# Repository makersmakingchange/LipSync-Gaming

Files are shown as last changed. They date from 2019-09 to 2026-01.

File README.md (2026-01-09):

## LipSync Gaming

> [!IMPORTANT]
**As of 2024-Feb-08, this version of the LipSync is now obsolete and has been replaced by the [LipSync 4](https://github.com/makersmakingchange/LipSync).**

The LipSync Gaming is an assistive technology device that allows quadriplegics and other people with limited hand function to use touchscreen mobile devices, tablets, and computers by manipulation of a mouth-operated joystick with integrated sip and puff controls. This is an Open-Source Hardware project, so the LipSync can be made at the community level for less than $300.

## Compatibility 

 <table style="width:100%">
  <tr>
    <th>Operating Systems</th>
    <th>Version</th>
    <th>Release</th>
    <th>Additional Information</th>
  <tr>
    <td>iOS</td>
    <td>13.1</td>
    <td>September 19,2019</td>
    <td>Compatible with iPhone 7 and newer versions (Requires USB to Lightning or USB to USB-C Adapter)</td>
  </tr>
  <tr>
    <td>Windows</td>
    <td>XP,7,10</td>
    <td>2001</td>
    <td>Compatible with Windows XP and newer versions</td>
  </tr>
  <tr>
    <td>Android</td>
    <td>4-9</td>
    <td>Released 2013</td>
    <td>Compatible with Android 4 and newer versions (Requires USB On-The-Go)</td>
  </tr>
  <tr>
    <td>MacOS</td>
    <td>10</td>
    <td>Released 2000</td>
    <td>Compatible with Mac OS X 10.0 and newer versions</td>
  </tr>
  </table> 

## Download

 <table style="width:100%">
  <tr>
    <th>Resource</th>
    <th>Version</th>
    <th>Format</th>
    <th>Link</th>
  </tr>
    <tr>
    <td>LipSync Gaming All</td>
    <td>3.0</td>
    <td>ZIP</td>
    <td><a href="https://github.com/makersmakingchange/LipSync-Gaming/archive/refs/heads/main.zip">LipSync-Gaming.zip</a></td>
  </tr>
  <tr>
    <td>LipSync Assembly Guide</td>
    <td>1.6</td>
    <td>PDF</td>
    <td><a href="https://github.com/makersmakingchange/LipSync-Gaming/blob/main/Documentation/LipSync_Assembly_Guide.pdf">LipSync_Assembly_Guide.pdf</a></td>
  </tr>
  <tr>
    <td>LipSync Gaming Startup Guide</td>
    <td>1.4</td>
    <td>PDF</td>
    <td><a href="https://github.com/makersmakingchange/LipSync-Gaming/blob/main/Documentation/LipSync_Gaming_Startup_Guide.pdf">LipSync_Gaming_Startup_Guide.pdf</a></td>
  </tr>
  <tr>
    <td>LipSync Gaming User Guide</td>
    <td>1.4</td>
    <td>PDF</td>
    <td><a href="https://github.com/makersmakingchange/LipSync-Gaming/blob/main/Documentation/LipSync_Gaming_User_Guide.pdf">LipSync_Gaming_User_Guide.pdf</a></td>
  </tr>
  <tr>
     <td>LipSync Gaming Mounting Guide</td>
     <td>1.0</td>
     <td>PDF</td>
     <td><a href="https://github.com/makersmakingchange/LipSync-Gaming/blob/main/Documentation/LipSync_Mounting_Guide.pdf">LipSync_Mounting_Guide.pdf</a></td>
  </tr>
  <tr>
    <td>LipSync Gaming BOM (XLSX)</td>
    <td>September 1, 2021</td>
    <td>XLSX</td>
    <td><a href="https://github.com/makersmakingchange/LipSync-Gaming/blob/main/Documentation/LipSync_Gaming_BOM.xlsx">LipSync_Gaming_BOM.xlsx</a></td>
  </tr>
  <tr>
    <td>LipSync Gaming BOM (CSV)</td>
    <td>September 1, 2021</td>
    <td>CSV</td>
    <td><a href="https://github.com/makersmakingchange/LipSync-Gaming/blob/main/Documentation/LipSync_Gaming_BOM.csv">LipSync_Gaming_BOM.csv</a></td>
  </tr>
  <tr>
    <td>LipSync Gaming Firmware</td>
    <td>3.0</td>
    <td>INO</td>
    <td><a href="https://raw.githubusercontent.com/makersmakingchange/LipSync-Gaming/main/Software/LipSync_Gaming_Firmware/LipSync_Gaming_Firmware.ino">LipSync_Gaming_Firmware.ino</a></td>
  </tr>
  <tr>
    <td>LipSync Gaming Interface Board Layout</td>
    <td>2.71</td>
    <td>BRD</td>
    <td><a href="https://github.com/makersmakingchange/LipSync-Gaming/raw/main/Hardware/PCB_design/Eagle/LipSync_Interface_Board/LipSync_Interface_Board.brd">LipSync_Interface_Board.brd</a></td>
  </tr>
  <tr>
    <td>LipSync Gaming Interface Board Schematic</td>
    <td>2.71</td>
    <td>SCH</td>
    <td><a href="https://raw.githubusercontent.com/makersmakingchange/LipSync-Gaming/main/Hardware/PCB_design/Eagle/LipSync_Interface_Board/LipSync_Interface_Board.sch">LipSync_Interface_Board.sch</a></td>
  </tr>
  <tr>
    <td>JLCPCB LipSync Gaming Interface Board Gerber</td>
    <td>2.71</td>
    <td>ZIP</td>
    <td><a href="https://github.com/makersmakingchange/LipSync-Gaming/raw/main/Hardware/PCB_design/Gerber/LipSync_Interface_Board/JLCPCB_LipSync_Interface_Board.zip">JLCPCB_LipSync_Interface_Board.zip</a></td>
  </tr>
  <tr>
    <td>OSHPark LipSync Gaming Interface Board Gerber</td>
    <td>2.71</td>
    <td>ZIP</td>
    <td><a href="https://github.com/makersmakingchange/LipSync-Gaming/raw/main/Hardware/PCB_design/Gerber/LipSync_Interface_Board/OSHPark_LipSync_Interface_Board.zip">OSHPark_LipSync_Interface_Board.zip</a></td>
  </tr>
  <tr>
    <td>PCBWay LipSync Gaming Interface Board Gerber</td>
    <td>2.71</td>
    <td>ZIP</td>
    <td><a href="https://github.com/makersmakingchange/LipSync-Gaming/raw/main/Hardware/PCB_design/Gerber/LipSync_Interface_Board/PCBWay_LipSync_Interface_Board.zip">PCBWay_LipSync_Interface_Board.zip</a></td>
  </tr>
  <tr>
    <td>Seeed Fusion LipSync Gaming Interface Board Gerber</td>
    <td>2.71</td>
    <td>ZIP</td>
    <td><a href="https://github.com/makersmakingchange/LipSync-Gaming/raw/main/Hardware/PCB_design/Gerber/LipSync_Interface_Board/Seeed_Fusion_LipSync_Interface_Board.zip">Seeed_Fusion_LipSync_Interface_Board.zip</a></td>
  </tr>
  <tr>
    <td rowspan="9">Housing_design</td>
    <td rowspan="9">3.0</td>
    <td rowspan="9">STL</td>
    <td><a href="https://github.com/makersmakingchange/LipSync-Gaming/blob/main/Hardware/Housing_design/LipSync_Button.stl">LipSync_Button.STL</a></td>
  </tr>
  <tr>
  <td><a href="https://github.com/makersmakingchange/LipSync-Gaming/blob/main/Hardware/Housing_design/LipSync_Front_Housing.STL">LipSync_Front_Housing.STL</a></td>
  </tr>
  <tr>
	<td><a href="https://github.com/makersmakingchange/LipSync-Gaming/blob/main/Hardware/Housing_design/LipSync_Joystick_Base.STL">LipSync_Joystick_Base.STL</a></td>
</tr>
<tr>
  <td><a href="https://github.com/makersmakingchange/LipSync-Gaming/blob/main/Hardware/Housing_design/LipSync_Joystick_Front.STL">LipSync_Joystick_Front.STL</a></td>
</tr>
<tr>
  <td><a href="https://github.com/makersmakingchange/LipSync-Gaming/blob/main/Hardware/Housing_design/LipSync_Joystick_Rocker.STL">LipSync_Joystick_Rocker.STL</a></td>
</tr>
<tr>
    <td><a href="https://github.com/makersmakingchange/LipSync-Gaming/blob/main/Hardware/Housing_design/Optional/LipSync_Joystick_Jig.STL">LipSync_Joystick_Jig.STL</a></td>
</tr>
<tr>
  <td><a href="https://github.com/makersmakingchange/LipSync-Gaming/blob/main/Hardware/Housing_design/LipSync_Rear_Housing.STL">LipSync_Rear_Housing.STL</a></td>
</tr>
<tr>
  <td><a href="https://github.com/makersmakingchange/LipSync-Gaming/blob/main/Hardware/Housing_design/3D_Print_Settings.txt">3D_Print_Settings.txt</a></td>
</tr>
</table> 

## Resources

<table style="width:100%">
  <tr>
    <th>Resource</th>
    <th>Link</th>
  </tr>
  <tr>
    <td>LipSync Firmware and Calibration Video</td>
    <td><a href="https://www.youtube.com/watch?v=RnpA24WH0Qk">Video</a></td>
  <tr>
    <td>LipSync Joystick Calibration Video</td>
    <td><a href="https://www.youtube.com/watch?v=Daf-54y6SBg">Video</a></td>
  </tr>
    <tr>
    <td>LipSync Build Video</td>
    <td><a href="https://www.youtube.com/watch?v=lBXpbkp5DW4&list=PLhoPg9bDvBR4CSFRfNbQ87ALnfaHOyM3C">Video</a></td>
  </tr>
</table> 

## License
Copyright (c) 2018-2024 Neil Squire / Makers Making Change.

This repository describes Open Hardware:
 - Everything needed or used to design, make, test, or prepare the LipSync Gaming is licensed under the [CERN 2.0 Weakly Reciprocal license (CERN-OHL-W v2) or later](https://cern.ch/cern-ohl ) .
 - All software is under the [GNU General Public License v3.0 (GPL-3.0)](https://www.gnu.org/licenses/gpl.html).
 - Accompanying material such as instruction manuals, videos, and other copyrightable works that are useful but not necessary to design, make, test, or prepare the LipSync are published under a [Creative Commons Attribution-ShareAlike 4.0 license (CC BY-SA 4.0)](https://creativecommons.org/licenses/by-sa/4.0/) .

You may redistribute and modify this documentation and make products using it under the terms of the [CERN-OHL-W v2](https://cern.ch/cern-ohl).
This documentation is distributed WITHOUT ANY EXPRESS OR IMPLIED WARRANTY, INCLUDING OF MERCHANTABILITY, SATISFACTORY QUALITY AND FITNESS FOR A PARTICULAR PURPOSE.
Please see the CERN-OHL-W v2 for applicable conditions.

Source Location: https://github.com/makersmakingchange/LipSync-Wireless

## Attribution

The LipSync Gaming was designed by Neil Squire Society / Makers Making Change. The initial development of a 3D printable LipSync was supported by the Google Impact Challenge: Disabilities grant from Google.org. Further development was supported through the Government of Canada's Innovation Science and Economic Development Assistive Technology Program. These and other funders have also enabled Neil Squire / Makers Making Change to deploy numerous LipSyncs to users at reduced cost.

The LipSync firmware utilizes the Arduino development platform, an open-source electronics platform based on easy-to-use hardware and software. Arduino is developed and maintained by the Arduino community, and the project wouldn't be possible without their contributions.
Arduino is a registered trademark of Arduino AG. For more information about Arduino and to contribute to the community, visit the official Arduino website at www.arduino.cc.

### Contributors
 - Milad Hajihassan, Neil Squire Society / Makers Making Change.
 - Jake McIvor, Neil Squire Society / Makers Making Change.
 - Kristina Mok, Neil Squire Society / Makers Making Change.
  
----

<!-- ABOUT MMC START -->
## About Makers Making Change
[Makers Making Change Logo](https://www.makersmakingchange.com/)

Makers Making Change is a program of [Neil Squire](https://www.neilsquire.ca/), a Canadian non-profit that uses technology, knowledge, and passion to empower people with disabilities.

Makers Making Change leverages the capacity of community based Makers, Disability Professionals and Volunteers to develop and deliver affordable Open Source Assistive Technologies.

 - Website: [www.MakersMakingChange.com](https://www.makersmakingchange.com/)
 - GitHub: [makersmakingchange](https://github.com/makersmakingchange)
 - Bluesky: [@makersmakingchange.bsky.social](https://bsky.app/profile/makersmakingchange.bsky.social)
 - Instagram: [@makersmakingchange](https://www.instagram.com/makersmakingchange)
 - Facebook: [makersmakechange](https://www.facebook.com/makersmakechange)
 - LinkedIn: [Neil Squire Society](https://www.linkedin.com/company/neil-squire-society/)
 - Thingiverse: [makersmakingchange](https://www.thingiverse.com/makersmakingchange/about)
 - Printables: [MakersMakingChange](https://www.printables.com/@MakersMakingChange)

### Contact Us
For technical questions, to get involved, or to share your experience we encourage you to [visit our website](https://www.makersmakingchange.com/) or [contact us](https://www.makersmakingchange.com/s/contact).
<!-- ABOUT MMC END -->

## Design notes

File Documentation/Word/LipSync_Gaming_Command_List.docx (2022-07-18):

## LipSync Gaming Command List

Command | Success Response | Failure Response | Description
SETTINGS | SUCCESS,0:SETTINGS | FAIL,{N}: Command | Enter Settings mode
EXIT | SUCCESS,0:EXIT | FAIL,{N}: Command | Exit Settings mode
MN,0:0 | SUCCESS,0:MN,0:2 | FAIL,{N}:Command | Get Model number (2=Gaming)
VN,0:0 | SUCCESS,0:VN,0:V{N.NN} | FAIL,{N}:Command | Get version number (V{N.NN})
SS,0:0 | SUCCESS,0:SS,0:{Joystick Sensitivity Level} | FAIL,{N}:Command | Get the joystick sensitivity value (Level)
SS,1:{Joystick Sensitivity Level:0-10} | SUCCESS,0:SS,1:{Joystick Sensitivity Level} | FAIL,{N}:Command | Set the joystick sensitivity value (Level)
| MANUAL,0:SS,1:{Joystick Sensitivity Level} | | Set the joystick sensitivity value (Level)
PT,0:0 | SUCCESS,0:PT,0:{Threshold 5% to 50%}:{Nominal Pressure V*100} | FAIL,{N}:Command | Get puff pressure threshold (threshold 5% to 50%) (Nominal Pressure)
PT,1:{threshold 10% to 50%} | SUCCESS,0:PT,1:{Threshold 5% to 50%}:{ Nominal Pressure V*100} | FAIL,{N}:Command | Set puff pressure threshold (threshold 5% to 50%) (Nominal Pressure)
ST,0:0 | SUCCESS,0:PT,0:{Threshold 5% to 50%}:{Nominal Pressure V*100} | FAIL,{N}:Command | Get sip pressure threshold (threshold 5% to 50%) (Nominal Pressure)
ST,1:{threshold 5% to 50%} | SUCCESS,0:PT,1:{Threshold 5% to 50%}:{ Nominal Pressure V*100} | FAIL,{N}:Command | Set sip pressure threshold (threshold 5% to 50%) (Nominal Pressure)
PV,0:0 | SUCCESS,0:PV,0:{Nominal Pressure} | FAIL,{N}:Command | Get pressure value (Nominal Pressure)
RA,0:0 | SUCCESS,0:RA,0:{Rotation Angle} | FAIL,{N}:Command | Get rotation angle (deg)
RA,1:{Angle: 0-359} | SUCCESS,0:RA,1:{Rotation Angle} | FAIL,{N}:Command | Set rotation angle (0,90,180,270 deg)
DM,0:0 | SUCCESS,0:DM,0:{Debug Mode} | FAIL,{N}:Command | Get debug mode value ( 0=debug mode disabled,1=debug mode enabled)
DM,1:0 | SUCCESS,0:DM,1:0 | FAIL,{N}:Command | Set debug mode value to 0 (Disabled)
DM,1:1 | SUCCESS,0:DM,1:1 | FAIL,{N}:Command | Set debug mode value to 1 (Enabled)
| LOG,1:{0,0,0,xHighNeutral,xLowNeutral,yHighNeutral,yLowNeutral} | | Log initialization values once if debug mode is enabled
| LOG,2:{0,0,0,xHighMax,xLowMax,yHighMax,yLowMax} | | Log calibration values once if debug mode is enabled
| LOG,3:{x,y,action,xHigh,xLow,yHigh,yLow} | | Log cursor and FSR values if debug mode is enabled until debug mode is disabled
IN,0:0 | SUCCESS,0:IN,0:{xHighNeutral,xLowNeutral,yHighNeutral,yLowNeutral} | FAIL,{N}:Command | Get joystick initialization values (xHighNeutral,xLowNeutral,yHighNeutral,yLowNeutral)
IN,1:1 | SUCCESS,0:IN,1:{xHighNeutral,xLowNeutral,yHighNeutral,yLowNeutral} | FAIL,{N}:Command | Perform joystick initialization using command (xHighNeutral,xLowNeutral,yHighNeutral,yLowNeutral)
| MANUAL,0:IN,1:{xHighNeutral,xLowNeutral,yHighNeutral,yLowNeutral} | | Perform joystick initialization using push button or sip/puff (xHighNeutral, xLowNeutral,yHighNeutral,yLowNeutral)
JV,0:0 | SUCCESS,0:JV,0:{xHigh,xLow,yHigh,yLow} | FAIL,{N}:Command | Get joystick FSR values: {xHigh,xLow,yHigh,yLow}
CA,0:0 | SUCCESS,0:CA,0:{xHighMax,xLowMax,yHighMax,yLowMax} | FAIL,{N}:Command | Get joystick calibration values (xHighMax,xLowMax,yHighMax,yLowMax)
CA,1:1 | SUCCESS,0:CA,1:0 | FAIL,{N}:Command | Perform joystick calibration using command
| SUCCESS,0:CA,1:1 | FAIL,{N}:Command | Perform joystick calibration using command (Step 1)
| SUCCESS,0:CA,1:2 | FAIL,{N}:Command | Perform joystick calibration using command (Step 2)
| SUCCESS,0:CA,1:3 | FAIL,{N}:Command | Perform joystick calibration using command (Step 3)
| SUCCESS,0:CA,1:4 | FAIL,{N}:Command | Perform joystick calibration using command (Step 4)
| SUCCESS,0:CA,1:5:{xHighMax,xLowMax,yHighMax,yLowMax} | FAIL,{N}:Command | Perform joystick calibration using command (Step 5) (xHighMax,xLowMax,yHighMax,yLowMax)
| MANUAL,0:CA,1:0 | | Perform joystick calibration using push button
| MANUAL,0:CA,1:1 | | Perform joystick calibration using push button (Step 1)
| MANUAL,0:CA,1:2 | | Perform joystick calibration using push button (Step 2)
| MANUAL,0:CA,1:3 | | Perform joystick calibration using push button (Step 3)
| MANUAL,0:CA,1:4 | | Perform joystick calibration using push button (Step 4)
| MANUAL,0:CA,1:5:{xHighMax,xLowMax,yHighMax,yLowMax} | | Perform joystick calibration using push button (Step 5) (xHighMax,xLowMax,yHighMax,yLowMax)
MP,0:0 | SUCCESS,0:MP,0:{NNNNNN} | FAIL,{N}:Command | Get Button mapping ( Example: SUCCESS,0:MP,0:125670)
MP,1: {NNNNNN} | SUCCESS,0:MP,1:{NNNNNN} | FAIL,{N}:Command | Set Button mapping ( Example: MP,1:125670)
DZ,0:0 | SUCCESS,0:DZ,0:{Deadzone Value} | FAIL,{N}:Command | Get the deadzone value
DZ,1:{ Deadzone :30-250} | SUCCESS,0:DZ,1:{ Deadzone Value} | FAIL,{N}:Command | Set the deadzone value ( Example: SUCCESS,0:DZ,1:30)
BM,0:0 | SUCCESS,0:BM,0:{Button Mode Value} | FAIL,{N}:Command | Get the button mode value (1 = Digital Mode , 2 = Analog Mode)
BM,1:{ Button Mode Value:1-2} | SUCCESS,0:BM,1:{Button Mode Value} | FAIL,{N}:Command | Set the button mode value (1 = Digital Mode , 2 = Analog Mode)
FR,1:{Rest Type: 0-1} | SUCCESS,0:FR,1:{Reset Type: 0-1} | FAIL,{N}:Command | Perform factory reset (0 = Hard Reset , 1 = Soft Reset)

## API Format

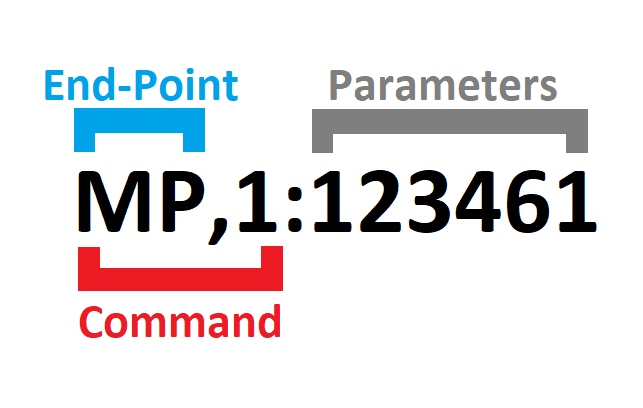
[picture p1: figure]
The API format which includes the end-point, command ,and the parameters.

## Response Code

Response Status | Response Code | Description
SUCCESS | 0 | The command has successfully performed.
FAIL | 0 | The serial API mode is not enabled. Please enter the serial API mode.
FAIL | 1 | The requested command does not exist. Returns the response code and the requested parameter.
FAIL | 2 | The requested command exists, but the entered parameter is in incorrect format. Returns the response code and the requested parameter.
FAIL | 3 | The requested command exists, but the entered parameter is out of range. Returns the response code and the current value stored in the EEPROM.

## Input Actions

Input Action | Description
Short Puff | < 3 seconds
Short Sip | < 3 seconds
Long Puff | 3-5 seconds
Long Sip | 3-5 seconds
Very Long Puff | > 5 seconds
Very Long Sip | > 5 seconds

## Output Digital Actions

Action Number | Output Action | Description
0 | (No action) | No action
1 | Button 1 Click | Presses and immediately releases Button 1.
2 | Button 2 Click | Presses and immediately releases Button 2.
3 | Button 3 Click | Presses and immediately releases Button 3.
4 | Button 4 Click | Presses and immediately releases Button 4.
5 | Button 5 Click | Presses and immediately releases Button 5.
6 | Button 6 Click | Presses and immediately releases Button 6.
7 | Center Reset | Initiates center reset routine to set joystick center position.
8 | Calibration | Initiates joystick calibration routine to set joystick limits and reset joystick center.

## Output Analog Actions

Action Number | Output Action | Description
0 | (No action) | No action
1 | Button 1 Press | Presses Button 1.
2 | Button 2 Press | Presses Button 2.
3 | Button 3 Press | Presses Button 3.
4 | Button 4 Press | Presses Button 4.
5 | Button 5 Press | Presses Button 5.
6 | Button 6 Press | Presses Button 6.
7 | Center Reset | Initiates center reset routine to set joystick center position.
8 | Calibration | Initiates joystick calibration routine to set joystick limits and reset joystick center.

## Digital Action Mapping

Input Action | LipSync Gaming Action
Short Puff | 1 : Button 1 Press and Release
Short Sip | 2 : Button 2 Press and Release
Long Puff | 5 : Button 5 Press and Release
Long Sip | 6 : Button 6 Press and Release
Very Long Puff | 7 : Center Reset
Very Long Sip | 0 : No action

## Analog Action Mapping

Input Action | LipSync Gaming Action
Puff | 1 : Button 1 Press
Sip | 2 : Button 2 Press

## Example

INPUT | RESPONSE | ACTION
SETTINGS | SUCCESS,0:SETTINGS | LipSync Ready for API Command
VN,0:0 | SUCCESS,0:VN,0:30 | LipSync return firmware version 3.0

INPUT | RESPONSE | ACTION
SETTINGS | SUCCESS,0:SETTINGS | LipSync Ready for API Command
PT,0:0 | SUCCESS,0:PT,0:10 | LipSync return current puff pressure threshold of 10%
PT,1:20 | FAIL,0:PT,1:20 | (Attempt to set puff pressure threshold failed – need to resend SETTINGS for each command)
SETTINGS | SUCCESS,0:SETTINGS | LipSync Ready for API Command
PT,1:20 | SUCCESS,0:PT,1:20:266 | LipSync set new puff pressure threshold of 20% and returned current nominal pressure of

Makers Making Change LipSync Gaming Command List

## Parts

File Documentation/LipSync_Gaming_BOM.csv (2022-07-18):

Qty | Component | Component name (September 1, 2021) | Line Item | Manufacturer | COO | MPN | SKU | SKU | SKU | SKU | SKU | SKU | SKU | SKU | URL ( Canada ) | URL ( United States )
 |  |  |  |  |  |  | Digi-Key | Mouser | Qosina | Cole-Parmer | Lee Spring | U.S. Plastic Corp. | B&H Photo | Amazon
1 | Required | Arduino Micro | A000053 | Arduino | Italy | A000053 | 1050-1066-ND | 782-A000053 |  |  |  |  |  |  | https://www.digikey.ca/product-detail/en/arduino/A000053/1050-1066-ND | https://www.digikey.com/product-detail/en/arduino/A000053/1050-1066-ND
2 | Required | Right Angle Push Button | "431256058736" | Würth Elektronik | China | "431256058736" | 431256058736-ND |  |  |  |  |  |  |  | http://www.digikey.ca/product-detail/en/wurth-electronics-inc/431256058736/431256058736-ND | https://www.digikey.com/product-detail/en/wurth-electronics-inc/431256058736/431256058736-ND
2 | Required | 300 Ohm 1/4W Axial Through-Hole Resistor | CF14JT300R | Stackpole Electronics | China | CF14JT300R | CF14JT300RCT-ND |  |  |  |  |  |  |  | https://www.digikey.ca/product-detail/en/stackpole-electronics-inc/CF14JT300R/CF14JT300RCT-ND | https://www.digikey.com/product-detail/en/stackpole-electronics-inc/CF14JT300R/CF14JT300RCT-ND
4 | Required | 10k Ohm 1/4W Mini Axial Through-Hole Resistor | CFM14JT10K0 | Stackpole Electronics | China | CFM14JT10K0 | S10KQCT-ND |  |  |  |  |  |  |  | https://www.digikey.ca/product-detail/en/stackpole-electronics-inc/CFM14JT10K0/S10KQCT-ND/ | https://www.digikey.com/product-detail/en/stackpole-electronics-inc/CFM14JT10K0/S10KQCT-ND/
1 | Required | Pressure Transducer | MPXV7002DPT1 | NXP Semiconductors | Malaysia | MPXV7002DPT1 | MPXV7002DPT1CT-ND | 841-MPXV7002DP |  |  |  |  |  |  | https://www.digikey.ca/product-detail/en/freescale-semiconductor-nxp/MPXV7002DPT1/MPXV7002DPT1CT-ND | https://www.digikey.com/product-detail/en/freescale-semiconductor-nxp/MPXV7002DPT1/MPXV7002DPT1CT-ND
1 | Required | 0.01 uF Ceramic Through-Hole Radial Capacitor | C315C103K5R5TA | KEMET | Mexico | C315C103K5R5TA | 399-4148-ND | 80-C315C103K5R |  |  |  |  |  |  | http://www.digikey.ca/product-detail/en/kemet/C315C103K5R5TA7303/399-9858-1-ND | http://www.digikey.com/product-detail/en/kemet/C315C103K5R5TA7303/399-9858-1-ND
1 | Required | 1.0 uF Ceramic Through-Hole Radial Capacitor | C315C105K3R5TA | KEMET | Mexico | C315C105K3R5TA | 399-9714-ND | 80-C315C105K3R |  |  |  |  |  |  | http://www.digikey.ca/product-detail/en/kemet/C315C105K3R5TA/399-9714-ND | http://www.digikey.com/product-detail/en/kemet/C315C105K3R5TA/399-9714-ND
1 | Required | 470 pF Ceramic Through-Hole Radial Capacitor | C315C471K5R5TA | KEMET | Mexico | C315C471K5R5TA | 399-9740-ND | 80-C315C471K5R |  |  |  |  |  |  | http://www.digikey.ca/product-detail/en/kemet/C315C471K5R5TA/399-9740-ND | http://www.digikey.com/product-detail/en/kemet/C315C471K5R5TA/399-9740-ND
2 | Required | 17-Position Straight Female Through-Hole Headers | PPPC171LFBN-RC | Sullins | Taiwan | PPPC171LFBN-RC | S7050-ND |  |  |  |  |  |  |  | http://www.digikey.ca/product-detail/en/sullins-connector-solutions/PPPC171LFBN-RC/S7050-ND | http://www.digikey.com/product-detail/en/sullins-connector-solutions/PPPC171LFBN-RC/S7050-ND
2 | Required | 3-Position Right Angle Male Through-Hole Header | 22-05-2031 | Molex | Mexico | 22-05-2031 | WM4101-ND |  |  |  |  |  |  |  | https://www.digikey.ca/product-detail/en/molex-connector-corporation/22-05-2031/WM4101-ND/ | https://www.digikey.com/product-detail/en/molex-connector-corporation/22-05-2031/WM4101-ND/
2 | Required | 3-Position Straight Female Through-Hole Header | 801-87-003-10-001101 | Preci-Dip | Switzerland | 801-87-003-10-001101 | 1212-1180-ND |  |  |  |  |  |  |  | https://www.digikey.ca/product-detail/en/preci-dip/801-87-003-10-001101/1212-1180-ND | https://www.digikey.com/product-detail/en/preci-dip/801-87-003-10-001101/1212-1180-ND
2 | Required | 4-Position Straight Female Through-Hole Header | PPPC041LFBN-RC | Sullins | Taiwan | PPPC041LFBN-RC | S7037-ND |  |  |  |  |  |  |  | http://www.digikey.ca/product-detail/en/sullins-connector-solutions/PPPC041LFBN-RC/S7037-ND | https://www.digikey.com/product-detail/en/sullins-connector-solutions/PPPC041LFBN-RC/S7037-ND
1 | Required | 40-Position Breakaway Straight Male Through-Hole Headers | PRPC040SAAN-RC | Sullins | Taiwan | PRPC040SAAN-RC | S1011EC-40-ND |  |  |  |  |  |  |  | http://www.digikey.ca/product-detail/en/sullins-connector-solutions/PRPC040SAAN-RC/S1011EC-40-ND | http://www.digikey.com/product-detail/en/sullins-connector-solutions/PRPC040SAAN-RC/S1011EC-40-ND
1 | Required | 5mm Bi-Color Through-Hole LED | MV5437 | Everlight Electronics Co Ltd | China | MV5437 | 1080-1109-ND |  |  |  |  |  |  |  | https://www.digikey.ca/product-detail/en/everlight-electronics-co-ltd/MV5437/1080-1109-ND/2675600 | https://www.digikey.com/product-detail/en/everlight-electronics-co-ltd/MV5437/1080-1109-ND/2675601
1 | Required | Jumper Shunt Connector | SSC02SYAN | Sullins | Taiwan | SSC02SYAN | S9002-ND |  |  |  |  |  |  |  | https://www.digikey.ca/product-detail/en/sullins-connector-solutions/SPC02SYAN/S9002-ND | https://www.digikey.com/product-detail/en/sullins-connector-solutions/SPC02SYAN/S9002-ND
1 | Required | 2N3906 PNP-type Through-Hole Transistor | 2N3906TFR | Fairchild Semiconductor | China | 2N3906TFR | 2N3906D26ZCT-ND |  |  |  |  |  |  |  | http://www.digikey.ca/product-detail/en/fairchild-on-semiconductor/2N3906TFR/2N3906D26ZCT-ND | http://www.digikey.com/product-detail/en/fairchild-on-semiconductor/2N3906TFR/2N3906D26ZCT-ND
1 | Required | 6-Position Straight Female Through-Hole Header | PPPC061LFBN-RC | Sullins | Taiwan | PPPC061LFBN-RC | S7039-ND |  |  |  |  |  |  |  | https://www.digikey.ca/product-detail/en/sullins-connector-solutions/PPPC061LFBN-RC/S7039-ND | https://www.digikey.com/product-detail/en/sullins-connector-solutions/PPPC061LFBN-RC/S7039-ND
1 | Required | Sip and Puff Mouthpiece | "11648" | Qosina | USA | "80102" |  |  | "80102" |  |  |  |  |  | https://www.qosina.com/stepped-male-luer-lock-connector-80102 | https://www.qosina.com/stepped-male-luer-lock-connector-80102
1 | Required | Filter PTFE Hydrophobic 17 mm, 0.2 Micron | "28213" | Qosina | USA | "28213" |  |  | "28213" |  |  |  |  |  | http://www.qosina.com/hydrophobic-filter-with-female-luer-lock-inlet-male-luer-lock-outlet-28213 | http://www.qosina.com/hydrophobic-filter-with-female-luer-lock-inlet-male-luer-lock-outlet-28213
1 | Required | Luer Lock Fitting | RK-45508-32 | Cole-Parmer | USA | RK-45508-32 |  |  |  | RK-45508-32 |  |  |  |  | https://www.coleparmer.ca/i/cole-parmer-female-luer-bulkhead-1-4-28-unf-thread-to-3-32-hose-barb-pp-25-pk/4550832 | https://www.coleparmer.ca/i/cole-parmer-female-luer-bulkhead-1-4-28-unf-thread-to-3-32-hose-barb-pp-25-pk/4550832
4 | Required | Force Resistive Sensor | 30-49649 | Interlink Electronics | China | 30-49649 | 1027-1000-ND |  |  |  |  |  |  |  | http://www.digikey.ca/product-detail/en/interlink-electronics/30-49649/1027-1000-ND | http://www.digikey.com/product-detail/en/interlink-electronics/30-49649/1027-1000-ND
4 | Required | Screws Phillips Head M3 | NMS-308 | Würth Elektronik | China | 97790803211 | 732-13710-ND |  |  |  |  |  |  |  | https://www.digikey.ca/en/products/detail/w%C3%BCrth-elektronik/97790803211/10056393 | https://www.digikey.com/en/products/detail/w%C3%BCrth-elektronik/97790803211/10056393
6 | Required | Compression Spring | LC 016C 03 S | Lee Spring | China | LC 016C 03 S |  |  |  |  | LC 016C 03 S |  |  |  | https://www.leespring.com/compression-springs?search=LC016C03S | https://www.leespring.com/compression-springs?search=LC016C03S
2 | Required | Standoff M3 10mm | "25501" | Keystone | USA | "25501" | 36-25501-ND | 534-25501 |  |  |  |  |  |  | http://www.digikey.ca/product-detail/en/keystone-electronics/25501/36-25501-ND/ | http://www.digikey.com/product-detail/en/keystone-electronics/25501/36-25501-ND/
2 | Required | Standoff M3 15mm | "25503" | Keystone | USA | "25503" | 36-25503-ND | 534-25503 |  |  |  |  |  |  | http://www.digikey.ca/product-detail/en/keystone-electronics/25503/36-25503-ND/ | http://www.digikey.com/product-detail/en/keystone-electronics/25503/36-25503-ND/
1 | Required | Luer Lock Nut | 45509-04 | Cole-Parmer | USA | 45509-04 |  |  |  | 45509-04 |  |  |  |  | https://www.coleparmer.ca/i/cole-parmer-panel-mount-lock-nut-1-4-28-unf-black-nylon-25-pk/4550904 | https://www.coleparmer.ca/i/cole-parmer-panel-mount-lock-nut-1-4-28-unf-black-nylon-25-pk/4550904
4 | Required | Bumper | SJ-5003 (BLACK) | 3M | USA | SJ-5003 (BLACK) | SJ5003-0-ND | 517-SJ-5003BK |  |  |  |  |  |  | https://www.mouser.ca/ProductDetail/3M-Electronic-Specialty/SJ-5003-BLACK?qs=sGAEpiMZZMvlOED0T0kTWubpGv7E7tyx | https://www.digikey.com/product-detail/en/3m/SJ-5003-(BLACK)/SJ5003-0-ND/102574
4 | Required | Nut M3 | 4708 | Keystone Electronics | Taiwan | 4708 | 36-4708-ND |  |  |  |  |  |  |  | https://www.digikey.ca/product-detail/en/keystone-electronics/4708/36-4708-ND/4499301 | https://www.digikey.com/product-detail/en/keystone-electronics/4708/36-4708-ND/4499301
1 | Required | Tubing Tygon 3350 3/32" ID x 45mm | "57289" | Tygon® | USA | "57289" |  |  |  |  |  | "57289" |  |  | http://www.usplastic.com/catalog/item.aspx?itemid=31562&catid=864 | http://www.usplastic.com/catalog/item.aspx?itemid=31562&catid=864
2 | Required | Light Pipe | 51513030250F | Dialight | Malaysia | 51513030250F | 350-3746-ND | 645-515-1303-0250F |  |  |  |  |  |  | http://www.mouser.com/search/ProductDetail.aspx?r=645-515-1303-0250F | http://www.mouser.com/search/ProductDetail.aspx?r=645-515-1303-0250F
1 | Required | Threaded Insert 5/8”-27 | M-11 | WindTech | USA | M-11 |  |  |  |  |  |  | WIM11 |  | https://www.bhphotovideo.com/c/product/850285-REG/windtech_m_11_5_8_27_f_to_1_2_m_npt.html | https://www.adorama.com/wtm11.html
1 | Required | Threaded Adapter 5/8"-27 | Mic Adapter | CAMVATE | China | Mic Adapter |  |  |  |  |  |  |  | Mic Adapter | https://www.amazon.com/CAMVATE-Female-Male-Piece-Adapter/dp/B01GWVQ022 | https://www.amazon.com/CAMVATE-Female-Male-Piece-Adapter/dp/B01GWVQ022
1 | Required | USB Cable 3' or 6' | UUSBHAUB3RA | Startech | China | UUSBHAUB3RA |  |  |  |  |  |  |  | USB Cable 3' or 6' | https://www.amazon.ca/Startech-Com-UUSBHAUB3RA-Micro-Cable-Right/dp/B001AR4NC8 | https://www.amazon.com/StarTech-com-Micro-USB-Cable-UUSBHAUB3RA/dp/B001AR4NC8 | https://www.amazon.com/gp/huc/view.html?ie=UTF8&newItems=C50dc2962-6371-4880-bf41-06ac5db860d9%2C1 | https://www.amazon.com/gp/product/B01M18TDO1/ref=ox_sc_act_title_2?smid=A21TE5CLHZDYA7&psc=1
1 | Required | USB Splitter | USB Splitter | JIUWU | China | USB Splitter |  |  |  |  |  |  |  | USB Splitter | https://www.amazon.ca/Wpeng-Female-degree-Micro-Splitter/dp/B01M5F47SY | https://www.amazon.com/Micro-Female-Cable-Power-Splitter/dp/B00NSBVNCM
1 | Required | Cable Tie | 298-1021-ND | Panduit Corp | Singapore | PLT.6SM-M |  | 644-PLT.6SM-M |  |  |  |  |  |  | https://www.mouser.ca/ProductDetail/Panduit/PLT6SM-M | https://www.mouser.com/ProductDetail/Panduit/PLT6SM-M
1 | Optional | Magic Arm 11" and Clamp | ZC462800 | YKS / GkGk | China | ZC462800 |  |  |  |  |  |  |  | Magic Arm 11" and Clamp | https://www.amazon.com/GkGk-Articulating-Friction-Adjustable-Monitor/dp/B017HKJVL4/ | https://www.amazon.com/GkGk-Articulating-Friction-Adjustable-Monitor/dp/B017HKJVL4/

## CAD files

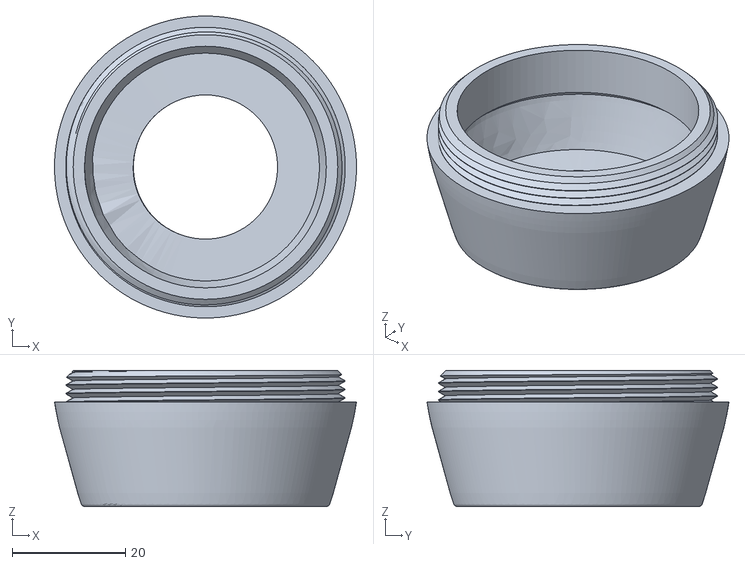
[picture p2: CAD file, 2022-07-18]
Hardware/Housing_design/LipSync_Front_Housing.STL
53.4 x 53.4 x 24.1

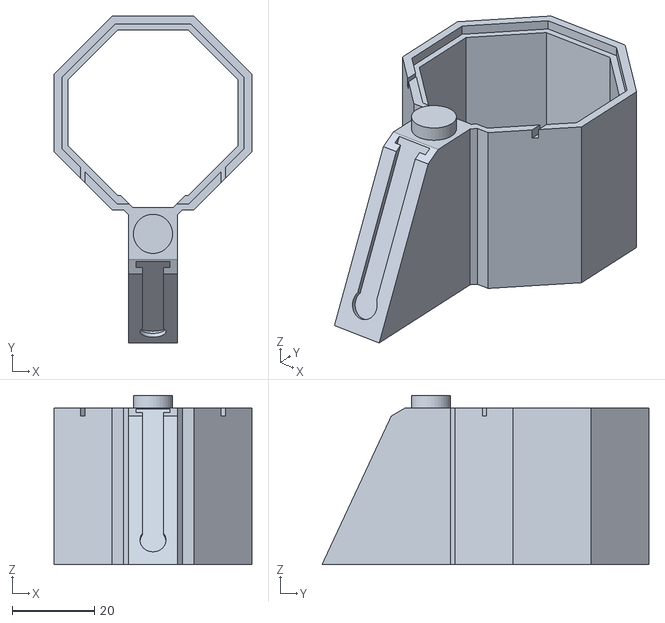
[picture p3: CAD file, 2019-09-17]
Hardware/Housing_design/Optional/LipSync_Joystick_Jig.STL
48.0 x 79.3 x 41.0

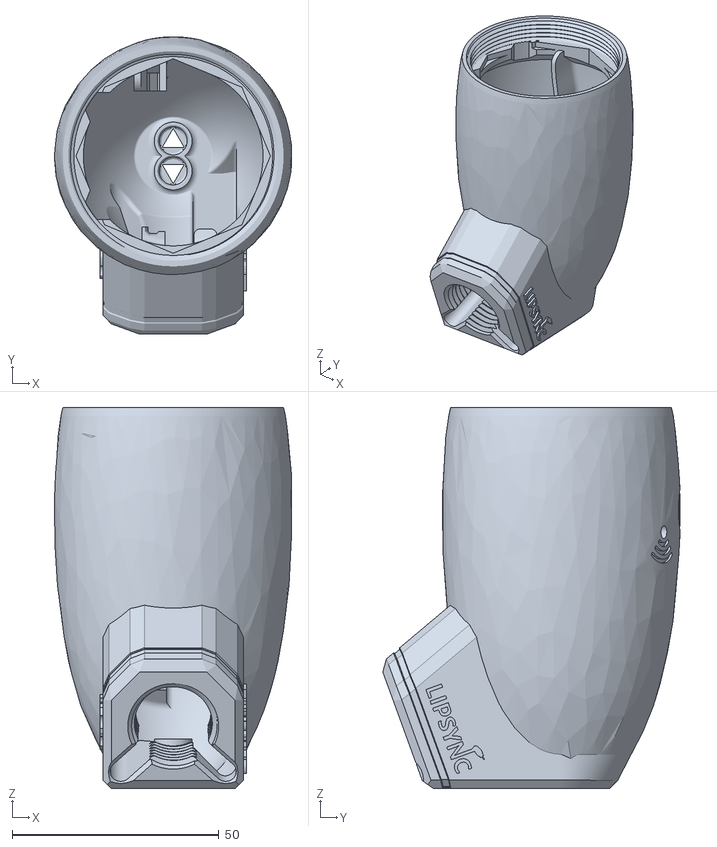
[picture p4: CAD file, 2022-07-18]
Hardware/Housing_design/LipSync_Rear_Housing.STL
57.5 x 72.0 x 92.2

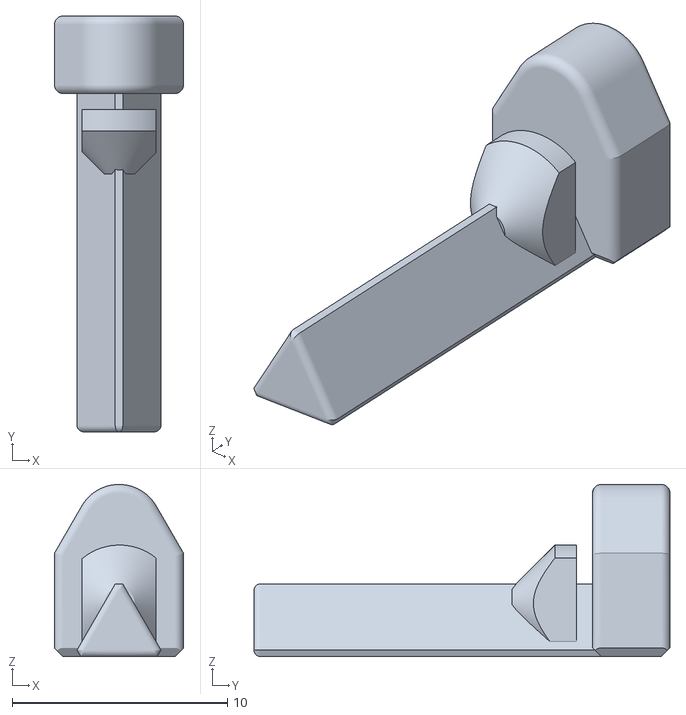
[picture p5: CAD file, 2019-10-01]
Hardware/Housing_design/LipSync_Button.stl
6.00 x 19.3 x 8.00

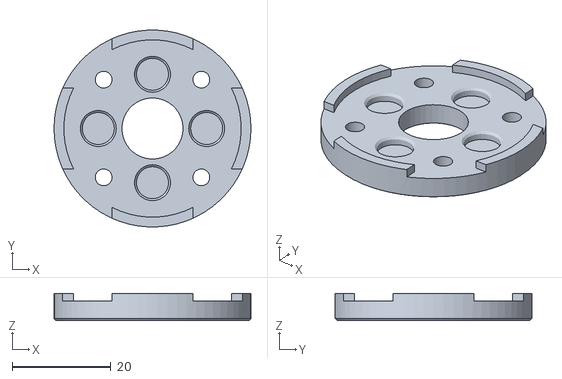
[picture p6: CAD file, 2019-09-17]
Hardware/Housing_design/LipSync_Joystick_Front.STL
40.0 x 39.9 x 5.50

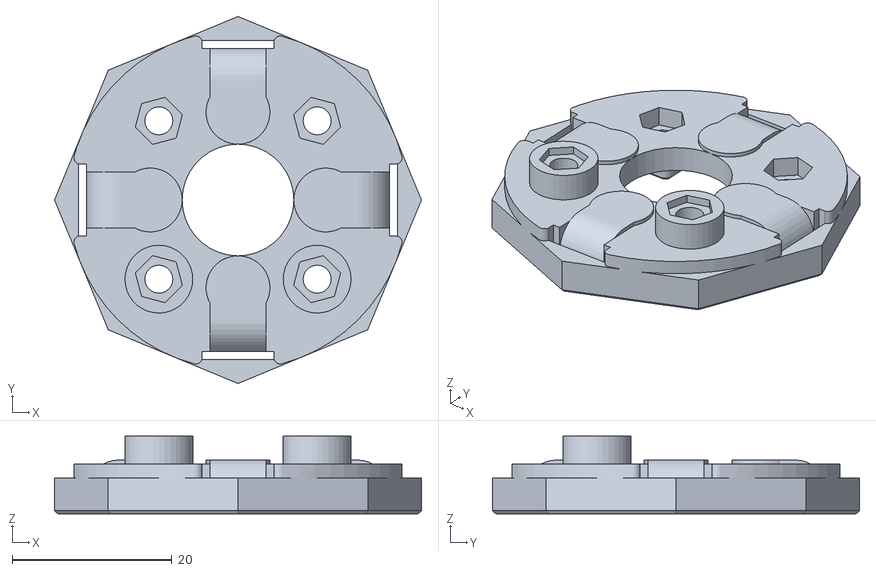
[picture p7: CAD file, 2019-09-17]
Hardware/Housing_design/LipSync_Joystick_Base.STL
46.0 x 46.0 x 9.75

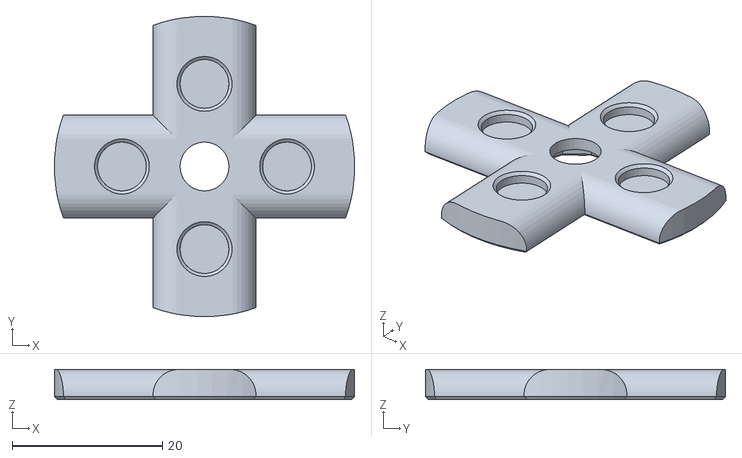
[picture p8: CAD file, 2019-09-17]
Hardware/Housing_design/LipSync_Joystick_Rocker.STL
40.0 x 40.0 x 4.00

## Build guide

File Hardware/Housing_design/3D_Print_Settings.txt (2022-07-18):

Print all components in orientation of STL file. Parts are designed to print with a 0.40 mm nozzle. Neutral, non-obtrusive filament colors (e.g. black, grey, white) are preferred for the rear housing and front housing unless the user requests otherwise. 

----------------------------
First print:
LipSync_Rear_Housing

Infill: 20%
Layer Height: 0.2mm
Support Material: No
Raft: No
Walls: 3
----------------------------

----------------------------
Second print:
1X LipSync_Front_Housing
2X LipSync_Button 
1X LipSync_Joystick_Stand (Optional; Recommended)

Infill: 20%
Layer Height: 0.2mm
Support Material: No
Raft: No
----------------------------

----------------------------
Third print:
1X LipSync_Joystick_Front_Plate
1X LipSync_Joystick_Rocker
1X LipSync_Joystick_Base

Infill: 50%
Layer Height: 0.2mm
Support Material: Yes
Raft: No
----------------------------

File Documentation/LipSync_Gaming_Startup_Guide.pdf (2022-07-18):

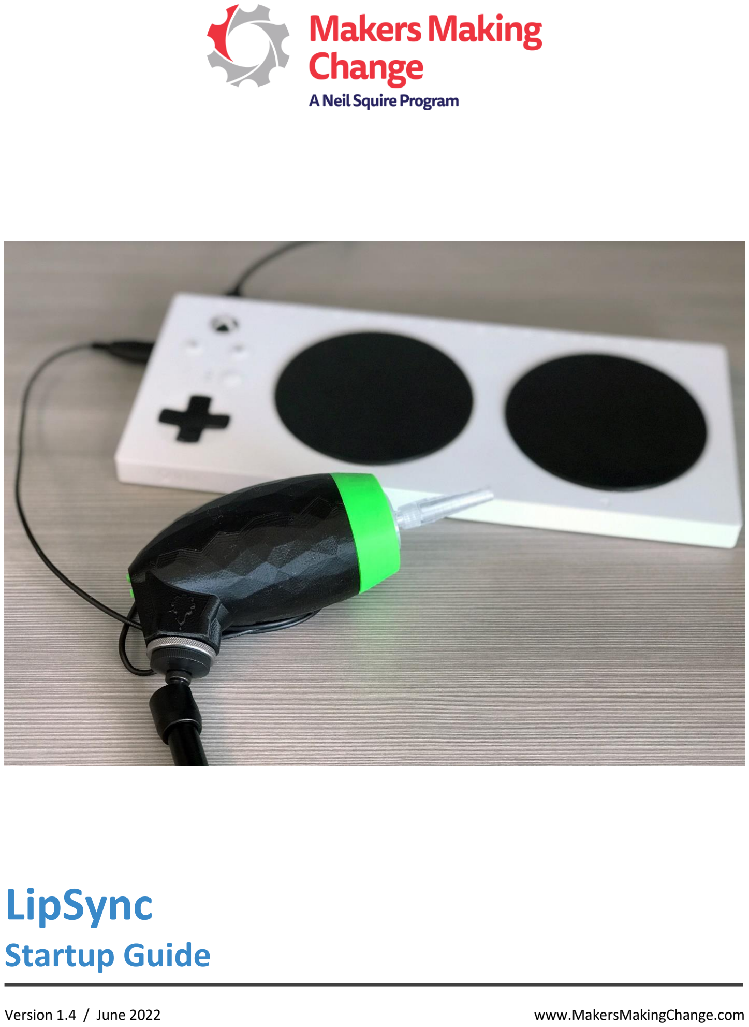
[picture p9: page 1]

# LipSync

# Startup Guide

Version 1.

4 / June 202

2 | www.MakersMakingChange.com

# Table of Contents

What Do You Get? | 3
Types of LipSync | 3
Mounting | 6
Device Compatibility | 7
Powering the Controller | 7
Sensitivity Control | 7
Setting Up for PC Gaming | 8
Functions (PC Games): | 8
Setting up for Xbox Gaming with the Xbox Adaptive Controller | 9
Functions (Xbox Adaptive Controller): | 9
Custom Profile | 10
Cleaning the Mouthpiece and Filter | 12
Cleaning the LipSync Shell | 13
Joystick Calibration | 14

# About the LipSync Gaming

The LipSync Gaming emulates a gaming controller for PC gaming and the Xbox console. Users can move the

mouthpiece up, down, left, and right; and use the sip-and-puff for other controller functions. This adaptive gaming

device is suitable for users with limited or no hand and finger dexterity. It can be paired with auxiliary controllers,

like the XBOX Adaptive Controller, to suit a gamer’s needs.

It is an open source assistive technology design by Makers Making Change, a program of the Neil Squire Society that

connects volunteer makers with people with disabilities to create more affordable assistive technology. Join the

Makers Makers Making Change to help people in your community: http://www.makersmakingchange.com

### What Do You Get?

### Types of LipSync

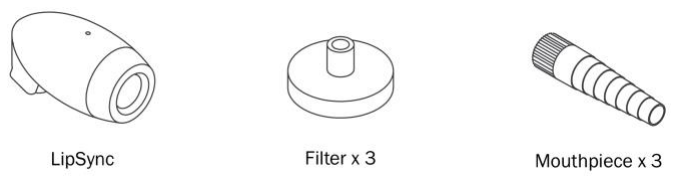
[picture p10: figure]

| Description | Connection Type
LipSync | Works like a mouse | USB
LipSync Wireless | Works like a mouse | Wireless
LipSync Macro | Works like a keyboard | USB & wireless
LipSync Gaming | Works like a gaming joystick | USB

# 1 LipSync Gaming Firmware Installation

1. Download and install the latest version of Arduino IDE: https://www.arduino.cc/en/main/software
2. Visit the LipSync Gaming firmware page: https://github.com/makersmakingchange/LipSync-

Gaming/raw/master/Software/LipSync_Gaming_Firmware/LipSync_Gaming_Firmware.ino (https://github.com/makersmakingchange/LipSync-Gaming/raw/master/Software/LipSync_Gaming_Firmware/LipSync_Gaming_Firmware.ino)

3. Right click on the webpage and select Save Page As. Add an .ino extension to the file name and click Save.
4. Visit the ArduinoJoystickLibrary GitHub repository using following link:

https://github.com/MHeironimus/ArduinoJoystickLibrary

5. Download the ArduinoJoystickLibrary by clicking on Clone or Download button and then selecting Download

ZIP option.

6. Extract the "ArduinoJoystickLibrary-master.zip" file.
7. Copy the Joystick folder to the Arduino libraries folder. An example of path to Arduino libraries folder in

Windows: C:\Program Files (x86)\Arduino\libraries

8. Once the folder is copied, the Joystick library should appear in the Arduino IDE list of libraries.
9. Plug the LipSync USB cable into the computer port.
10. Open Arduino IDE and you should be able to see Joystick examples under File > Examples > Joystick
11. Now open the LipSync_Gaming_Firmware.ino file using Arduino IDE.
12. Select Tools > Board > Arduino/Genuino Micro.
13. Select Tools > Port > COM## (number may be different for each user)
14. Click on upload button to upload the code.

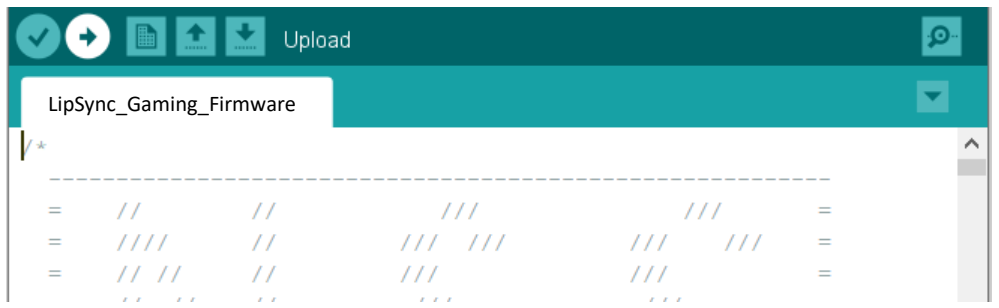
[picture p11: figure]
LipSync_Gaming_Firmware

15. With the LipSync Gaming plugged into a power source, perform the joystick calibration.

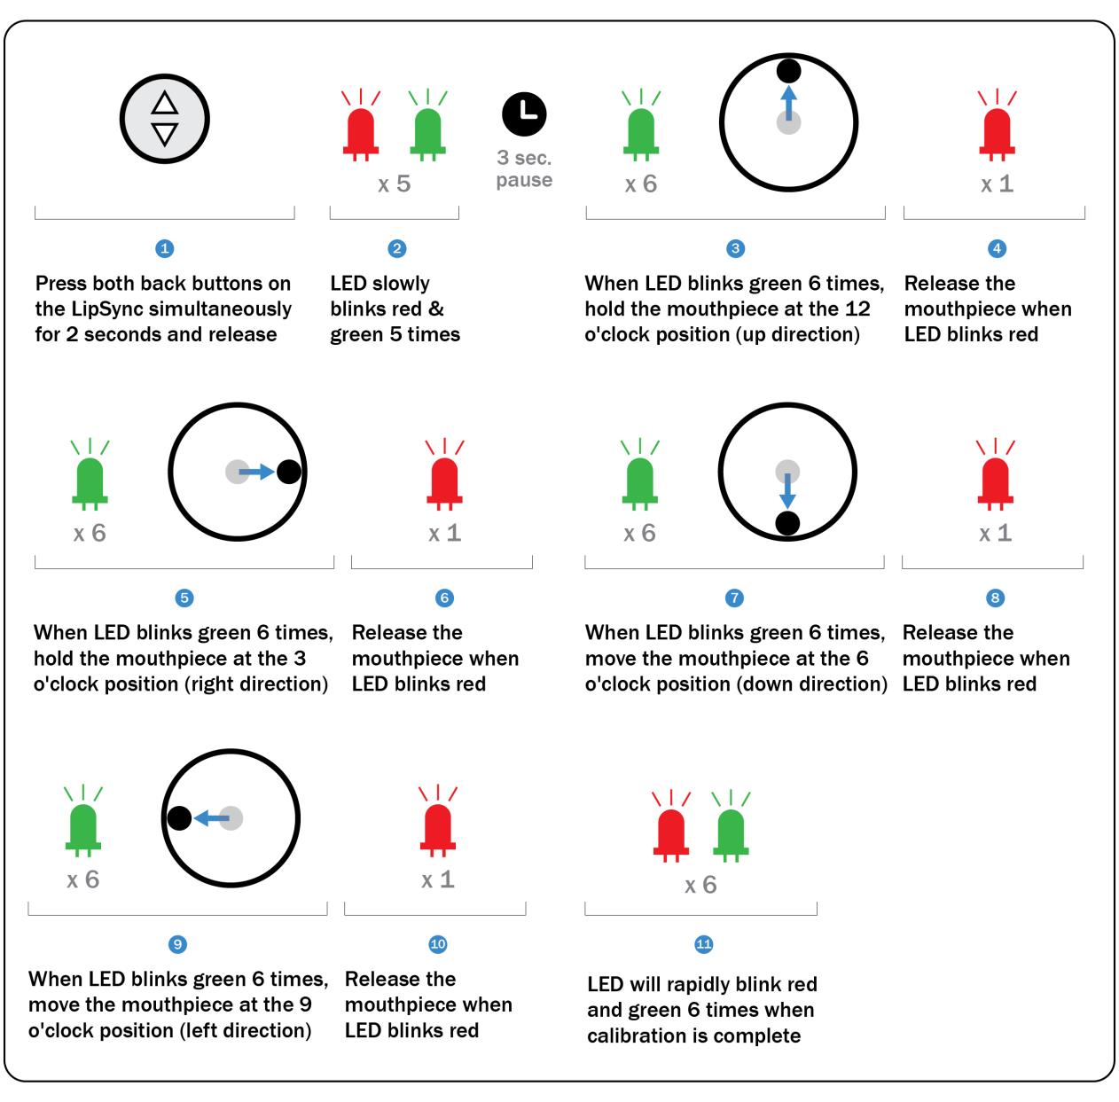
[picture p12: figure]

# 2 Getting Started

The LipSync Gaming requires the following items to get started:

- A LipSync Gaming
- External power bank (optional but recommended)
- Mounting solution for securing the LipSync to a surface

### Mounting

Wheelchair: Every wheelchair has different points available for mounting. Common mounting points available on

power wheelchairs are the headrest rail, back of wheelchair, armrest rail, under chair cushion, chair rail, and

footplate. Try out different areas and see what works best. If you are not familiar with mounts, consult with an

assistive technology professional.

Desk: Find a clear space on the front edge of your desk or table. Orient the mount bracket toward the user being

careful not to move the LipSync. Secure the bracket and adjust the mounting arm so the LipSync is within easy

reach. Tighten the knob when the arm is in the desired position.

Checklist for after mounting:

☐ Are the clamp and mount secure and do not move?

☐ Is there clearance around the wheels, wires, and chair frame with the mount attached?

☐ Does the wheelchair fit through doorways?

☐ Is the driving view of the user clear with no obstructions?

☐ Is the mobile device within viewing angle of the LipSync?

☐ Can the user easily reach the LipSync to use it?

### Device Compatibility

### Powering the Controller

The Adaptive Controller has an internal rechargeable battery that allows users to use it wirelessly. Using the LipSync

(and any external accessibility switch) will draw additional power. To prevent heavy power consumption, we

recommend plugging the Adaptive Controller into to an electrical outlet using an AC Adapter (Option 1) or a power

bank of at least 5000mAH (Option 2) using a USB to USB-C cable while gaming.

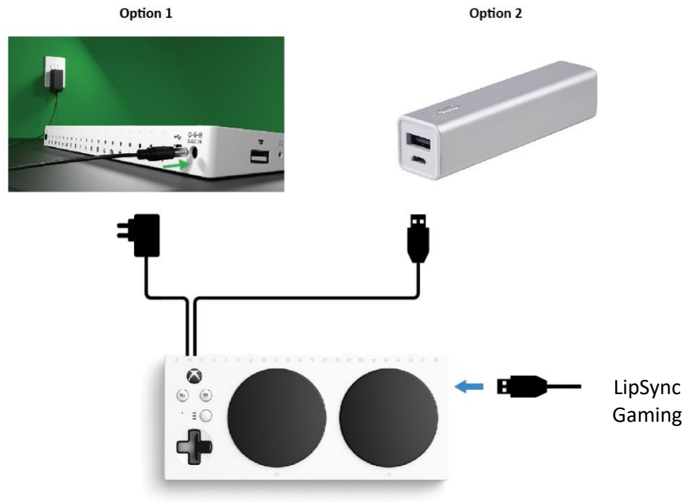
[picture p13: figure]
LipSync Gaming

### Sensitivity Control

The LipSync Gaming has 11 sensitivity levels with the default level set to 5 when first set up. The LED will blink the

sensitivity level number.

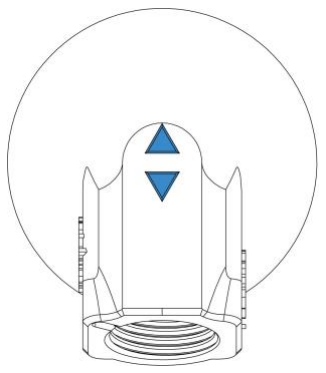
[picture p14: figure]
LipSync back view

Press the | button to increase the joystick sensitivity.
Press the | button to decrease the joystick sensitivity.

To adjust the sensitivity, set the device’s sensitivity level to its slowest setting to

start then adjust the LipSync Gaming sensitivity control buttons. If it’s still not fast

enough, gradually increase the sensitivity on the device.

Windows
MacOS
Xbox | Xbox Adaptive Controller
(only with the Xbox
Adaptive Controller)

# 3 PC and Xbox Gaming Setup

### Setting Up for PC Gaming

1. Plug the USB from the LipSync Gaming into any computer or laptop USB Port.
2. Start up the PC game.
3. Adjust the sensitivity of the sip-and-puff features by pressing the triangular speed buttons on the back of

the LipSync.

4. If any of the functions starts to drift or behave inconsistently while gaming, release the mouthpiece and

hold both buttons at the same time for 1 second to perform the joystick initialization.

### Functions (PC Games):

LipSync Action | Time (Seconds) | Mode 1 (Hold for 2 sec) ¹ | Mode 2 (Hold for 2 sec) ²
Mouthpiece (Up) | - | Move up | Move up
Mouthpiece (Down) | - | Move down | Move down
Mouthpiece (Left) | - | Move left | Move left
Mouthpiece (Right) | - | Move right | Move right
Puff | 1 | Button Number 1 | Button Number 1
Sip | 1 | Button Number 2 | Button Number 2
Puff | 3 | Button Number 5 | N/A
Sip | 3 | Button Number 6 | N/A
Puff | 5 | Centre reset | N/A
Sip | 5 | No action | N/A

1 LED will blink red and green 1 time

2 LED will blink red and green 2 times

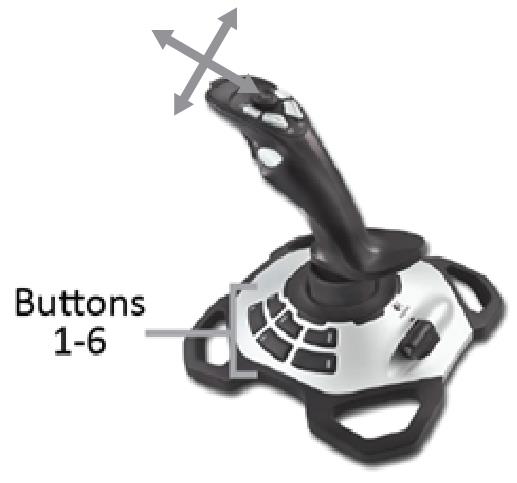
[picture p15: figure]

Left USB port

### Setting up for Xbox Gaming with the Xbox Adaptive Controller

1. Turn on your XBOX Console.
2. Turn on your Adaptive Controller by pressing the XBOX button .
3. Plug the LipSync USB Cable to the right or left USB port on either side of the Adaptive Controller. Each side

has different gaming functions so double check with the user.

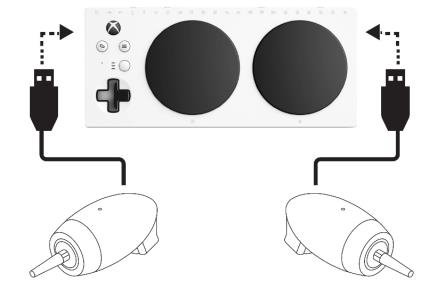
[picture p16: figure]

4. Adjust the sensitivity of the sip-and-puff features by pressing the triangular speed buttons on the back of

the LipSync.

5. If any of the functions starts to drift or behave inconsistently while gaming, release the mouthpiece and

hold both buttons at the same time for 1 second to perform the joystick initialization.

### Functions (Xbox Adaptive Controller):

The following Mode 2 functions (highlighted in orange) are default actions and can be modified in profile settings.
Action | Time (Sec) | Mode 1 (Left USB Port) (Hold for 2 sec)¹ | Mode 2 (Left USB Port) (Hold for 2 sec)² | Mode 1 (Right USB Port) (Hold for 2 sec)¹ | Mode 2 (Right USB Port) (Hold for 2 sec)²
Right | - | Move right | Move right | Move right | Move right
Down | - | Move down | Move down | Move down | Move down
Left | - | Move left | Move left | Move left | Move left
Up | - | Move up | Move up | Move up | Move up
Puff | 1 | X1 | X1 | View | View
Sip | 1 | X2 | X2 | Menu | Menu
Puff | 3 | A | N/A | X | N/A
Sip | 3 | B | N/A | Y | N/A
Puff | 5 | Centre reset | N/A | Centre reset | N/A
Sip | 5 | No action | N/A | No action | N/A

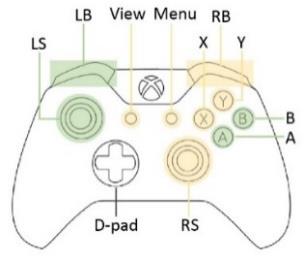
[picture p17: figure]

1 LED will blink red and green 1 time

2 LED will blink red and green 2 times

Right USB port

### Custom Profile

The Xbox Adaptive Controller comes with the option to

configure and map buttons using 3 different mapping

profiles. Switch between profiles by pressing on the Profile

Button or pressing the Shift button after it’s assigned in

settings. Please follow the instructions below to map the

buttons through the Profile settings:

1. Press the Xbox button to open the guide.

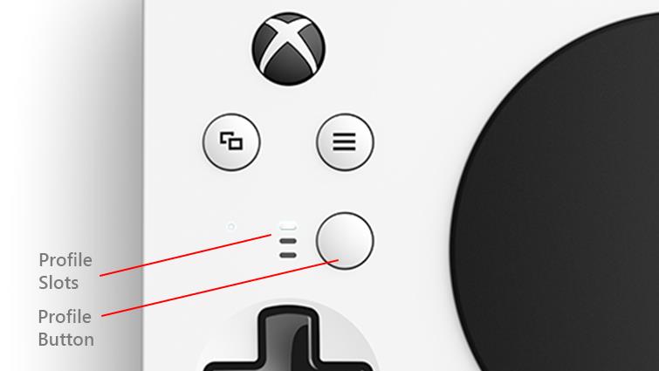
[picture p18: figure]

2. Select Home > Settings > Kinect and Devices > Devices & Accessories.
3. Press the A button (3 second puff) > Select Xbox Adaptive Controller.
4. Select Configure option > press the A button (3 second puff).
5. Select New profile > press the A button (3 second puff).
6. Enter the name for the new profile (Example: “LipSync1”).
7. Under the Mapping menu, select the Xbox controller button that you would like to map >press the A button (3

second puff).

8. Assign the Primary and Shift button actions for selected button > press the B button (3 second sip).

### 9. The following five examples can be used to map the main buttons:

- X1 button (1 second puff)
A. Under the Mapping menu, select the X1 button > press the A button (3 second puff).
B. Assign the Primary and the Shift button actions for selected X1 button.
C. The Primary button action is assigned to the A button and the Shift button action is assigned to

the X button for the X1 button in the LipSync1 profile example.

D. Press the B button (3 second sip).
- X2 button (1 second sip)
A. Under the Mapping menu, select the X2 button > press the A button (3 second puff).
B. Assign the Primary and the Shift button actions for selected X2 button.
C. The Primary button action is assigned to the B button and the Shift button action is assigned to

the Y button for the X2 button in the LipSync1 profile example.

D. Press the B button (3 second sip).
- A button (3 second puff)
A. Under the Mapping menu, select the A button > press the A button (1 second puff).
B. Assign the Primary and the Shift button actions for selected A button.
C. The Primary button action is assigned to the View button and the Shift button action is assigned

to the Menu button for the A button in the LipSync1 profile example.

D. Press the B button (3 second sip).

- B button (3 seconds puff)
A. Under the Mapping menu, select the B button > press the A button (1 second puff).
B. Assign the Primary and the Shift button actions for selected B button.
C. The Primary button action is assigned to the Menu button and the Shift button action is assigned

to the View button for the B button in the LipSync1 profile example.

D. Press the B button (3 second sip).
10. Under the Mapping menu, select the button that you would like to map to the Shift button action > press the A

button (1 second puff).

11. Select the Use as Shift button check box > press the A button (1 second puff) > press the B button (1 second sip).
12. Press the B button (1 second sip) to enter the Profiles page again.
13. Select the new created LipSync1 profile > press the A button (1 second puff).
14. Save the new profile by selecting the No Slot dropdown menu >press the A button (1 second puff).
15. Select one of the three available slots > press the A button (1 second puff).
16. The LipSync1 profile is now ready to use. Press the Profile button on the Xbox Adaptive Controller to switch

between profiles and select LipSync1 profile for these functions:

LipSync Action | Time (Seconds) | Mode 1 Primary | Mode 2 Secondary
Mouthpiece (Up) | - | Move up | Move up
Mouthpiece (Down) | - | Move down | Move down
Mouthpiece (Left) | - | Move left | Move left
Mouthpiece (Right) | - | Move right | Move right
Puff | 1 | A | X
Sip | 1 | B | Y
Puff | 3 | View | Menu
Sip | 3 | Menu | View
Puff | 5 | Centre reset | Centre reset
Sip | 5 | No action | No action

# 4 Maintenance

### Cleaning the Mouthpiece and Filter

Each user should have their own set of mouthpiece and filter for hygienic reasons. These pieces are made of acrylic

plastic and have a 3-6 month life cycle depending on the usage. Keep unused pieces in a clean sealable bag out of

the sunlight.

Follow these steps to clean the pieces during its life cycle:

1. With the LipSync facing you and wearing clean gloves, twist the mouthpiece and filter counter clockwise to

detach it. If you’re having trouble removing the filter, see the next page.

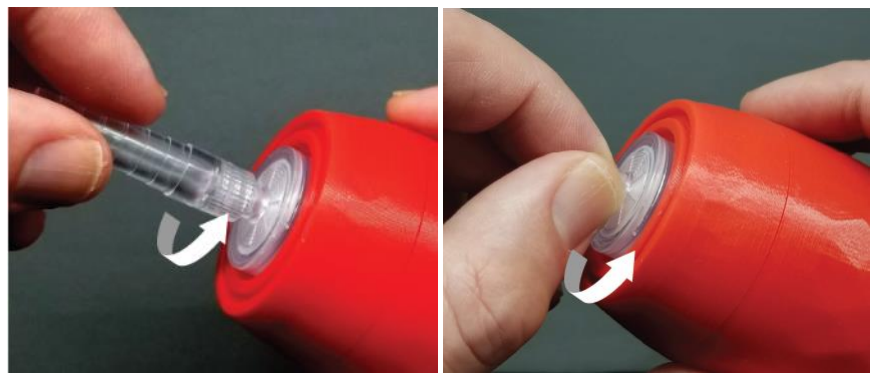
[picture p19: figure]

2. To clean the mouthpiece: mix 1 cup (250 mL) of water with 2 tsp (10 mL) of 5% bleach (sodium

hypochlorite). Soak the mouthpiece for 10 minutes and then air dry or wipe with a clean cloth.

To clean the filter: throw away used filters that have trapped saliva and use a clean piece.

3. Wearing clean gloves, twist the mouthpiece and filter clockwise until finger tight. Do not overtighten.

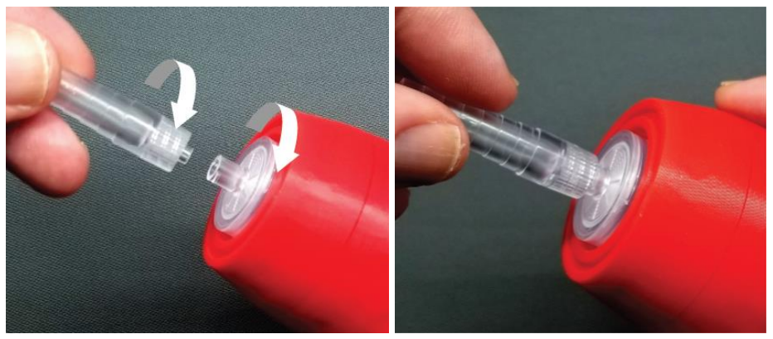
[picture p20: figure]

Broken stem removal

If you’re unable to screw in a new LipSync air filter, it may be because a portion of the old filter has broken off and is

stuck inside the air fitting. To remove this broken piece, the best tool to use is a medical hemostat or very small vice

grips. You can also use fine nose needle nose pliers, however, you’ll need to be more careful with pliers so as not to

not to break the plastic and make the problem worse.

To remove using a hemostat: Insert one side of the hemostat tip into the middle of the broken off filter stem and

the other side of the tip to the outside of the protruding broken stem. Be extra careful not to grip on the outside of

the fitting that it’s in or you will damage the LipSync. Squeeze the handle on the hemostat until the teeth between

the finger holes lock. Finally, rotate the tip of the hemostat counter-clockwise to remove the broken stem.

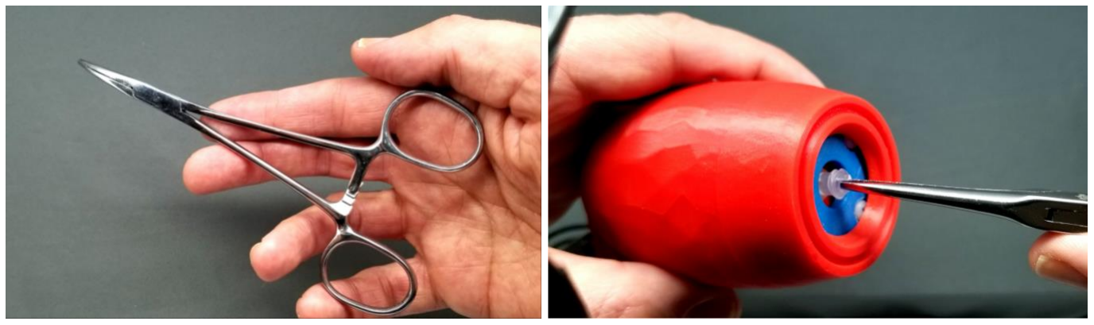
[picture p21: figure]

If a hemostat is not available, use an extra fine tip needle nose pliers or vice but be even more careful as these

larger tools can damage the LipSync easily.

### Cleaning the LipSync Shell

✓ | Wipe with a non-abrasive cloth lightly dampen with water or cleaning alcohol
✗ | Don’t use abrasive cleaning materials.
✗ | Don’t soak the LipSync shell in any cleaning solutions

# 5 Troubleshooting

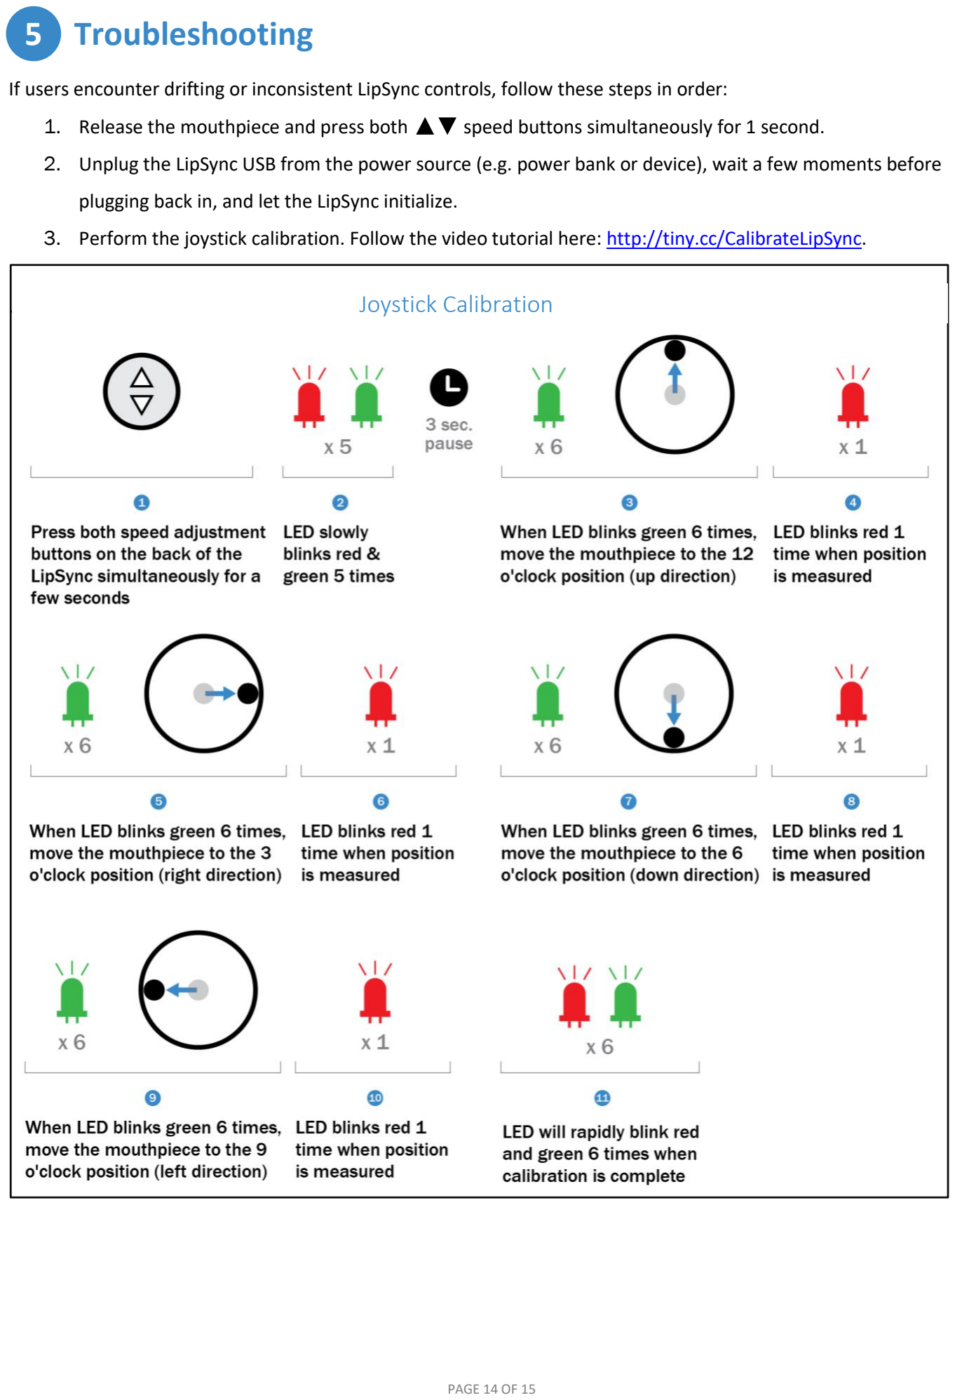
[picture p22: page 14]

If users encounter drifting or inconsistent LipSync controls, follow these steps in order:

1. Release the mouthpiece and press both speed buttons simultaneously for 1 second.
2. Unplug the LipSync USB from the power source (e.g. power bank or device), wait a few moments before

plugging back in, and let the LipSync initialize.

3. Perform the joystick calibration. Follow the video tutorial here: http://tiny.cc/CalibrateLipSync.

### Joystick Calibration

# 6 Feedback

The LipSync is an open-source project, which means that anyone and everyone is able to build the device and

improve upon the design. If you have suggestions for how to improve the LipSync or require technical help, please

reach out using one of the following routes:

1. Contact your LipSync maker
2. Makers Making Change Forum (https://makersmakingchange.com/forum/)
3. Makers Making Chance R&D team at info@makersmakingchange.com
4. Leave a review on the LipSync page (https://www.makersmakingchange.com/project/lipsync/)

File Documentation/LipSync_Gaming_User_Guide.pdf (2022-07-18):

Version 1.4 | June 2022


www.MakersMakingChange.com

# LipSync Gaming: User Guide

## Introduction

The LipSync Gaming emulates a gaming controller for PC gaming and the Xbox console. Users can move the LipSync mouthpiece up, down, left, and right; and use the sip-and-puff for other controller functions.

This adaptive gaming device is suitable for users with limited or no hand and finger dexterity. It can be paired with auxiliary controllers, like the Xbox Adaptive Controller, to suit a gamer’s needs.

## Device Compatibility

## Powering the Xbox Adaptive Controller

Using the LipSync (and any external accessibility switch) with the Xbox Adaptive Controller will draw additional power. Plug the XAC to a power bank or use an AC adapter.

## Connecting to the Xbox Adaptive Controller

Plug the LipSync USB into the
USB port on either side of the
Adaptive Controller. The left and right USB ports have
different gaming functions.
These can be remapped within

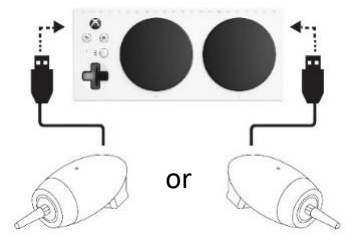
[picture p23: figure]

Xbox settings. See LipSync Gaming: Startup Guide for remapping instructions.

## Joystick Initialization

Perform the joystick initalization everytime before playing a game by releasing the mouthpiece and hold both
buttons on the back of the LipSync simultaneously for 1 second. If gaming functions start to drift, perform the same procedure as well.

## Default Functions for Adaptive Controller

Action | Time (sec) | Mode 1 (left USB port) 1 | Mode 2 (left USB port) 2 | Mode 1 (right USB port) 1 | Mode 2 (right USB port) 2
Up | - | Up | Up | Up | Up
Down | - | Down | Down | Down | Down
Left | - | Left | Left | Left | Left
Right | - | Right | Right | Right | Right
Puff | 1 | X1 | X1 | View | View
Sip | 1 | X2 | X2 | Menu | Menu
Puff | 3 | A | N/A | X | N/A
Sip | 3 | B | N/A | Y | N/A
Puff | 5 | Centre Reset | N/A | Centre Reset | N/A
Sip | 5 | N/A | N/A | N/A | N/A
1 Press the | button for 2 sec. for Mode 1. LED will blink red & green once.

2
Press the button for 2 sec. for Mode 2. LED will blink red & green twice.

## Connecting to the for PC

Plug the Lipsync USB directly into the PC’s USB port.

## Default Functions for PC

Action | Time (sec) | Mode 1 ¹ | Mode 2 ²
Up | N/A | Up | Up
Down | N/A | Down | Down
Left | N/A | Left | Left
Right | N/A | Right | Right
Puff | 1 | Button 1 | Button 1
Sip | 1 | Button 2 | Button 2
Puff | 3 | Button 5 | N/A
Sip | 3 | Button 6 | N/A
Puff | 5 | Centre Reset | N/A
Sip | 5 | N/A | N/A
1 Press the | button for 2 sec. for Mode 1. LED will blink red & green once.

2
Press the button for 2 sec. for Mode 2. LED will blink red & green twice.

Windows
MacOS

AC adapter

Xbox Adaptive
Controller

Xbox
(only with Xbox
Adaptive Controller)

Power bank
(>5000 mAh)

Version 1.4 | June 2022

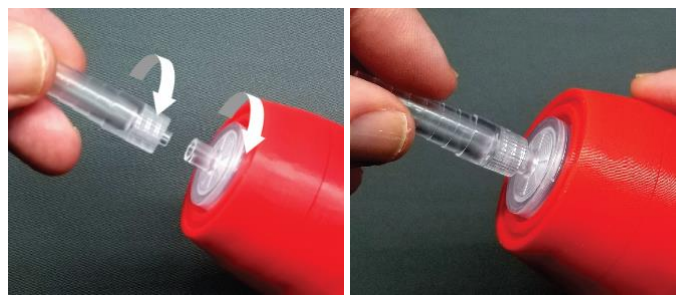
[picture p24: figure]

www.MakersMakingChange.com

1 | 2 | 3 | 4 | 5 | 6 | 7 | 8 | 9 | 10 | 11

## Sensitivity Control

Press the | button to increase the joystick sensivity.
Press the | button to decrease the joystick sensivity.

The LED will blink the sensitivity level number. The previous setting will be saved the next time the LipSync is used.

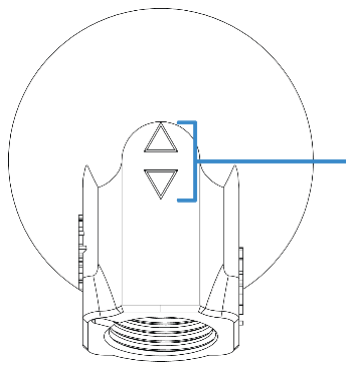
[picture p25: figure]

## Cleaning the Mouthpiece and Filter

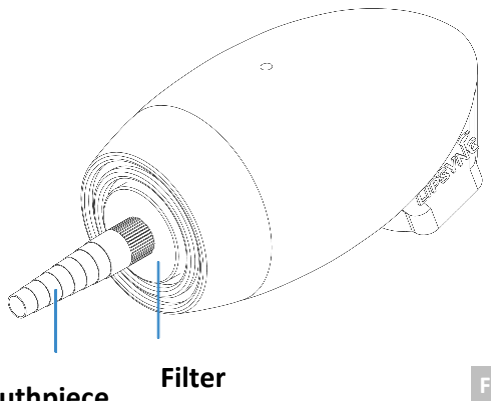
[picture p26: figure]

Each user should have their own set of mouthpiece and filter for hygienic reasons. These pieces are made of acrylic plastic and have a 3–6-month life cycle depending on the usage.

Follow these steps to clean the pieces during its life cycle:

1. With the LipSync facing you and wearing clean gloves, twist the mouthpiece and filter counter clockwise to remove them.
2. If the filter doesn’t twist off or the filter stem is broken, use a hemostat or extra fine tip needle nose pliers to grip and carefully twist it off. See the LipSync Gaming: Startup Guide for in-depth instructions.
3. To clean the mouthpiece: mix 1 cup (250 mL) of water with 2 tsp (10 mL) of 5% bleach (sodium hypochlorite). Soak it for 10 minutes and let it air dry or wipe with clean cloth.
To clean the filter: throw away used filters that have trapped saliva and use a clean piece.
4. Wearing clean gloves, twist the mouthpiece and filter clockwise until finger tight. Do not overtighten.

## Cleaning the LipSync Shell

✓ Wipe with a non-abrasive cloth lightly dampen with water or cleaning alcohol
✗ | Don’t use abrasive cleaning materials
✗ | Don’t soak the LipSync shell in any cleaning solutions

## Troubleshooting Cursor Issues

If users encounter drifting or inconsistent cursor movement, follow these steps in order:

1. Release the mouthpiece and press both speed buttons simultaneously for 1 second.
2. Unplug the LipSync USB from the power source (e.g. power bank or device), wait a few moments before plugging it back, and let the LipSync initialize.
3. Perform joystick calibration. See the last page on the LipSync Gaming: Startup Guide or watch the calibration tutorial on YouTube (https://tiny.cc/CalibrateLipSync).

If steps 1-3 doesn’t resolve the cursor issue, contact your LipSync maker or go to the Makers Making Change Forum (https://forum.MakersMakingChange.com) for assistance.

Most
Sensitive
Least | Default level
Sensitive

Sensitivity buttons
Adjusts sensitivity level

BACK VIEW

Filter Mouthpiece Traps saliva

Sip-and-puff tubing

FRONT VIEW

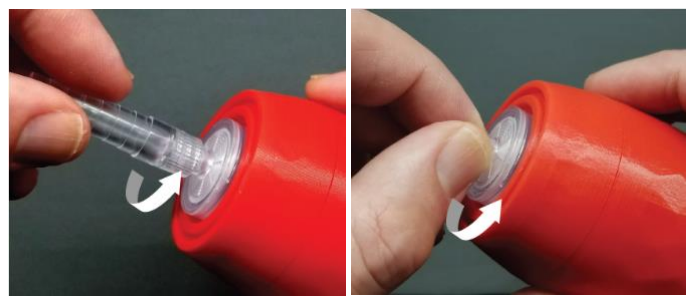
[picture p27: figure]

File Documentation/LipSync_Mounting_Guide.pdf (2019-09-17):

# MOUNTING THE LIPSYNC

## By: Manal Faour

## Contents

Introduction The LipSync is a mouth operated mouse replacement that allows people with severe mobility

impairments to use mobile devices such as a mobile phone. The lightness of the LipSync as well as its compactness make it a great candidate for portable, wheelchair mounted applications but some considerations need to be taken when choosing a mounting option to ensure ease of use and safety of the user. This document details the considerations of how to mount the LipSync. Now that you have the LipSync, how can you mount it onto a wheelchair? What options are there for your mobile device? What are some of the considerations to have in mind when choosing a mounting option?

## Mounting to a Wheelchair

## Mounting Points

Every wheelchair is different in terms of the points available for mounting. Below is a list of some common mounting points that are available on power wheelchairs. The sketches illustrate the locations of these mounting points on the wheelchair.
1. Headrest rail
2. Back of wheelchair
3. Armrest rail
4. Under chair cushion
5. Chair rail
6. Footplate

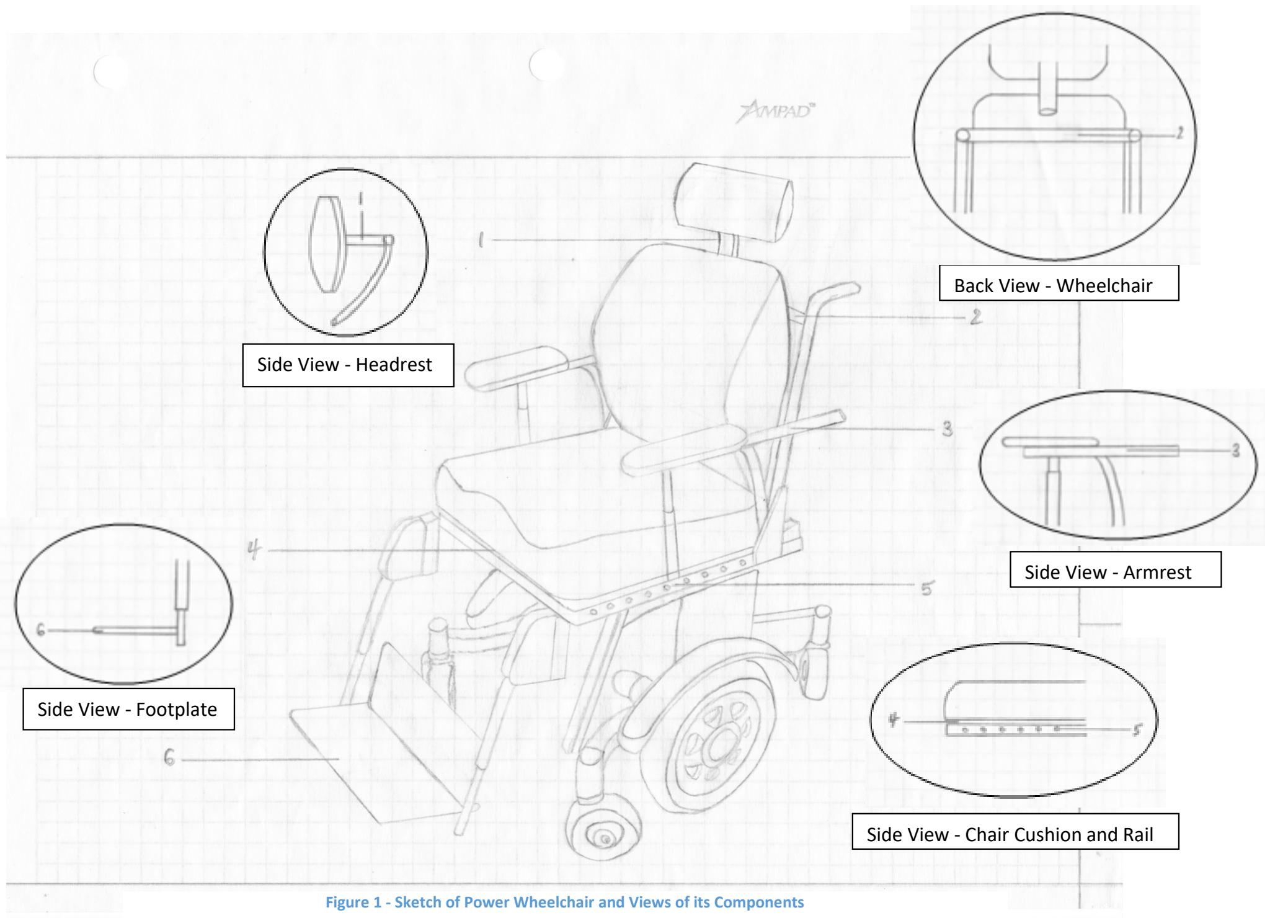
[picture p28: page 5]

Side View - Headrest

Side View - Armrest

Back View - Wheelchair

Side View - Chair Cushion and Rail

Side View - Footplate

Figure 1 - Sketch of Power Wheelchair and Views of its Components

## Considerations

When choosing a mount, many things need to be taken into consideration to ensure the safety of the user. Below you'll find a complete detailed list of these considerations. For a quick checklist, refer to Appendix A Checklist for After Choosing a Mount.
1. Mounting at the sides can make doorways difficult to navigate. Modern wheelchairs are 24"-27" in width and a wheelchair accessible door is usually 32" therefore care should be taken when mounting to the side of the wheelchair. Ensure that the addition of the mount at the sides of the wheelchair does not extend beyond the wheelchair frame to avoid hitting the doorway and potentially dislodging the mount, thereby putting the user at a safety risk. There is also a risk of the mount getting caught in obstacles. The image below demonstrates a setup that must be avoided as it can be easily snagged on something or could potentially bump into surrounding objects.

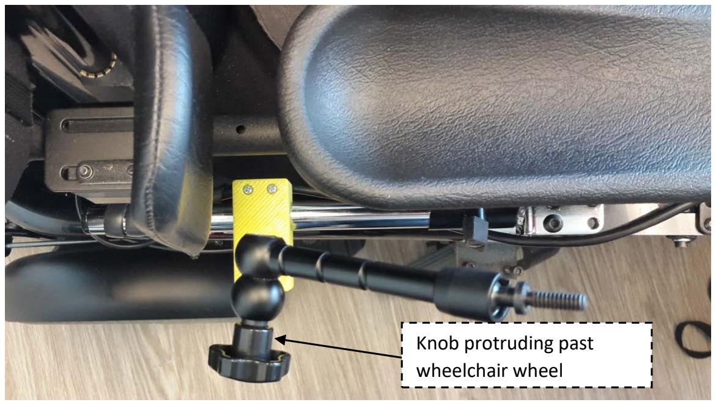
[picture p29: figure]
Knob protruding past wheelchair wheel

Figure 2 - Image of an Unacceptable Mount Setup
2. Attaching a clamp vertically may cause slipping of the mount. Therefore care must be taken when mounting in this direction.
3. To increase the friction and avoid slipping of a clamp additional anti skid pads may be added. A common product that is used for this purpose is Dycem, which provides reels of non-slip mats and tapes. Another option is "Magic Wrap" used for plumbing repairs.
4. Care should be taken when mounting to the headrest especially in reclining chairs. In a reclined position, the mount is more likely to detach and fall. Some solutions to this problem is increasing the friction of the mount using methods described above. Another solution is to choose a mount that completely encases the rail of the headrest as shown in the image below.

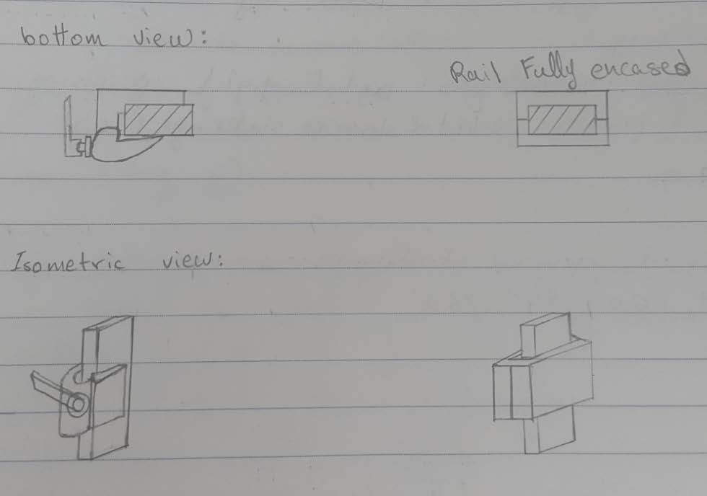
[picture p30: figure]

Figure 3 - A bottom and isometric view of a clamp that does not encase the rail vs. one that does
5. Wiring must be avoided to prevent faulty connections of the wheelchair devices.
6. Clearance around the wheels must be maintained to avoid detachment of the device or damage to the wheelchair.
7. In many wheelchairs, reclining causes a few components of the wheelchair to shift in position. Therefore, when choosing a mounting point check that there is clearance around the different components in both a reclined and non-reclined position.
8. When positioning the LipSync, care should be taken to ensure that the driving view of the user is not obstructed.
9. When positioning the LipSync, make sure that it is vertically aligned as described in Figure 4. Assemblies with goosenecks or ball and sockets at the top allow for positioning the LipSync vertically.

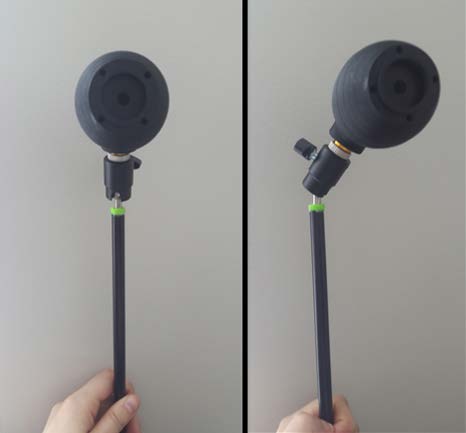
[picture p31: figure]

Figure 4 - Left: LipSync Positioned Vertically; Right: LipSync Positioned Non-vertically
10. When positioning the mobile device ensure that it is within viewing angle of the LipSync. The normal optical axis for a person in a sitting position is at 15° below eye level (Figure 4).
For example, if mounting a phone 35cm away from your face, the normal optical axis for a person in a sitting position is 15° below the 0° line, which translates to 7cm below eye level at that distance (Appendix D Field of Vision Claculations). The Limit of the range of vision is at 70-80°.

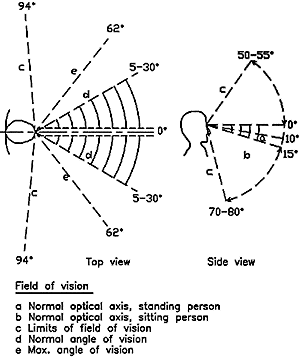
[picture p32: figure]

Figure 5 - Field of Vision Range ((SOLIDERE) & (ESCWA), 1994)
11. When positioning the mobile device, make sure that it is adjusted to avoid glare from the sun. In some cases, it may be necessary to add an anti-glare screen protector to the mobile device available here. (https://www.amazon.ca/Tech-Armor-Anti-Glare-Anti-Fingerprint-Protectors/dp/B00IGISQUO)
12. On some power wheelchairs, the armrest can be lifted to allow for transferring the wheelchair user. Therefore, mounting to that side of the wheelchair in those cases is not recommended.
13. Mounting at the back of the wheelchair requires the mount to be very long compared to other mounting points. In this position the mount experiences a large amount of torque which could cause it to fail.

Suppliers The following list is meant to serve as an introduction to suppliers that offer mounts that could be used

for the LipSync or a mobile device. The list is by no means exclusive since many other retailers sell mounts that work for our application either specific to assistive technology or not.

## On-Stage

https://on-stage.com/
On-Stage manufactures a range of stands for musical instruments and microphones. Advantages
a. It offers solutions at a lower price in comparison to the other suppliers.

Drawbacks
b. The goosenecks they offer are used for light weights and may sag under a heavy weight.
Sample Parts and Approximate Prices
Part No. | Description | Supplier | Qty | Approximate Cost (CAD)
MSA9030-19B | 19" Gooseneck, Black | Best Buy | 1 | $15
MSA9030-13B | 13" Gooseneck, Black | Best Buy | 1 | $10
MSA9030-06B | 6" Gooseneck, Black | Best Buy | 1 | $7
MSA9505 | Posi-Lock Telescoping Mini-Boom | Best Buy | 1 | $30

## Loc Line

http://www.loc-line.com/
Lockwood products inc manufactures Loc-Line - a range of adjustable plastic hoses and adaptors originally developed for cooling purposes in machine tool operations.
Advantages
a. Hand adjustable for both position and length.
b. Unique ball and socket design, bending does not decrease the inside diameter.
c. Can be twisted along its axis.
d. Easily washable and is resistant to most common chemicals.
e. Reasonably priced and is widely available.
f. Hollow so a wire can be fed through it.
g. Able to use for both the phone and the LipSync device using one setup (Y fitting). Drawbacks
a. Not suitable for applications where high loads are involved.
Sample Parts and Approximate Prices
* EH Pope is a Canadian distributor
Part No. | Description | Supplier | Qty | Approximate Cost (CAD)
Direct Mounting Solutions (to wheelchair)
510001 | Spring Clamp, 2", with integrated 3/4" ID Fixed Mount. Assembled. | Modular Hose | 1 | $9
512001 | Round Tube and Flat Surface Clamp Kit. | Modular Hose | 1 | $39
Extension Lines
61501 | Hose Segments Pack for 3/4" ID System. Includes (2) 5" long segments. Approximately 1 foot. | EH Pope | 1 | $7
51801 | Hose Segments Pack for 1/2" ID System. Includes (2) 5" long segments. Approximately 1 foot. | EH Pope | 1 | $6

## Ablenet

https://www.ablenetinc.com/technology/mounting-cases
Advantages
a. The mounts are all sold as a whole piece - no need to buy anything else.
b. Many available options from a gooseneck to mounting arms. Drawbacks
a. Relatively expensive.
Sample Parts and Approximate Prices
Part No. | Description | Supplier | Qty | Approximate Cost (CAD)
- | Latitude Mounting Arm (quick release) | Ablenet | 1 | $440
- | Gooseneck Mounting System | Ablenet | 1 | $250
- | Friction Knob Universal Mounting System | Ablenet | 1 | $325

## SnakeClamp

http://snakeclamp.com/Category/smartphone-snakeclamp-desk-stand-mount-holder-flexible-goosneck-arm (http://snakeclamp.com/Category/smartphone-snakeclamp-desk-stand-mount-holder-flexible-goosneck-arm)
Advantages
a. You have the option of building your own mount.
b. Heavy duty goosenecks are available.
Drawbacks
a. Goosenecks may be unstable and sag under heavy weight.
Sample Parts and Approximate Prices
Part No. | Description | Supplier | Qty | Approximate Cost (CAD)
Direct Mounting Solutions (to wheelchair)
SCP-MC | Multiclamp | SnakeClamp | 1 | $39
Extension Lines
SCP-GN24 | 24" Heavy Duty Flexible Gooseneck Arm | SnakeClamp | 1 | $39
SCP-GN18 | 18" Flexible Gooseneck Arm | SnakeClamp | 1 | $22
SCP-GN18HD | 18" Heavy-Duty Flexible Gooseneck Arm | SnakeClamp | 1 | $24
SCP-GN13B | 13" Flexible Gooseneck Arm, Black | SnakeClamp | 1 | $22
SCP-GN09 | 9" Flexible Gooseneck Arm | SnakeClamp | 1 | $14
SCP-RA12 | 12" Rigid Arm | SnakeClamp | 1 | $18

## Manfrotto

https://www.manfrotto.ca/
Manfrotto manufactures a range of clamps, adaptors and fixtures for mounting cameras, lighting devices and studio accessories.
Advantages
a. Load carrying capacity is relatively high.
Drawbacks
a. Cost is relatively high.
b. Electrically conductive.
c. Heavy, bulky and has a very 'industrial' appearance. Sample Parts and Approximate Prices
Part No. | Description | Load
capacity
(kg)

Max length
(mm)
Supplier | Qty | Approximate
Price (CAD)
Direct Mounting Solutions (to wheelchair)
171 | Mini clamp | 1 | - | Manfrotto | 1 | $40
035 | Super Clamp | 15 | - | Manfrotto | 1 | $57
635 | Quick Action Super Clamp | 15 | - | Manfrotto | 1 | $70
Extension Lines
244N | Variable friction arm | 3 | 530 | Manfrotto | 1 | $200
237 | Flex arm. ID 13mm. | 0.3 | 550 | Manfrotto | 1 | $50
237 HD | Heavy duty flex arm. ID 18mm. | 0.5 | 550 | Manfrotto | 1 | $60
196AB-2 | Single articulated arm: 2 sections | 1.5 | 605 | Manfrotto | 1 | $55

## LinkDelight

http://linkdelight.com/en/.html
LinkDelight offers a range of photography equipment. Advantages
a. Offers compact and small mounts.
Drawbacks
a. Mainly aimed at the photography industry therefore some adapters need to be purchased. Sample Parts and Approximate Prices
Part No. | Description | Supplier | Qty | Approximate Cost (CAD)
| 11" Magic Adjustable Arm for Lilliput Monitor / | Amazon | 1 | $15

LED Light Video Monitor
11" Articulating Magic Arm + Small Clamp Crab Pliers + Gopro Adapter+ Stainless Steel Thumber Screw Accessory Kit | LinkDelight | 1 | $24
Digital Camera Camcorder Mini Ballhead 1/4" Screw Thread Base | LinkDelight | 1 | $6
Mini Ball Head with Lock and Hot Shoe Adapter Camera | Amazon | 1 | $5

## Mobility Mount

http://www.mobilitymount.com/
Mobility Mount provides mounts specifically for wheelchair users. It's uniqueness lies in the fact that the base of the mount is held under the seat cushion. Many adapters are available to allow for mounting multiple devices.
Advantages
a. Mount sits under chair cushion therefore no mounting points necessary.
Disadvantages
a. Expensive to buy.
Sample Parts and Approximate Prices
Part No. | Description | Supplier | Qty | Approximate Cost (CAD)
MM01 | Base with tube | Mobility Mount | 1 | $320
MT | Multi Table 10X14 with no slip | Mobility Mount | 1 | $155
TC | Tablet Configuration for table | Mobility Mount | 1 | $115

Mounting Assemblies Below you'll find some wheelchair mounting options for the LipSync, a mobile device, or the

combination of both. Endless setups may be assembled to fit a the user's needs. Some setups may be more convenient than others depending on the considerations listed in the previous sections. Some of these components can be purchased from other suppliers.

## LipSync

The LipSync has a standard 5/8"-27 thread female connection. The mounting options below include a 5/8"-27 thread male connection in order to connect to the LipSync.

### Mounting Options Per Price Range

$0 - $49
Most of the options below include a 3D printed clamp which contributes to the reduced price. The downside of using 3D printed parts is the reduction in the strength of the component and the likelihood of it breaking if used to hold up a heavy weight.
For the assembly instructions of the 3D Printed Clamp refer to Appendix B Assembly Instructions for 3D Printed Clamp.
For assembly instruction of the DIY Mount refer to Appendix C Assembly Instructions for DIY Mount. Note: There are two possible assemblies for the DIY Mount. A Mini Ball Head with Lock may be used in cases where the articulating arm and the arrow shafts do not provide enough flexibility to position the LipSync vertically. Steps for both options are included below.
Part No. | Description | Qty | Supplier | Approximate Cost (CAD)

Total
Option 1 - DIY Mount
3D Printed Clamp + Nuts and Bolts | 1 | - | $3 | $3
Female 1/4"-20 to 5/8"-27 Male 2 Piece Mic Adapter | 1 | Amazon | $9 | $9
11" Inch Friction Articulating Magic Arm for Camera DSLR | 1 | Amazon | $14 | $14
3D Printed 1/4-20 threaded insert | 1 | - | $0 | $0
Arrow shaft | 1 | Local Archery Store/Walmart | $7 | $7
3D printed Disk Gear + Nut and Bolt | 1 | - | $2 | $2
3D Printed 3/8-16 threaded holder | 1 | - | $0 | $0
For the second possible assembly
Mini Ball Head with Lock and Hot Shoe Adapter Camera | 1 | Amazon | $5 | $5
1/4 male to 3/8 male adapter | 1 | Amazon | $7 | $7
3/8 female to 5/8 male adapter | 1 | Amazon | $7 | $7
| | | TOTAL | $35 (Or $54)

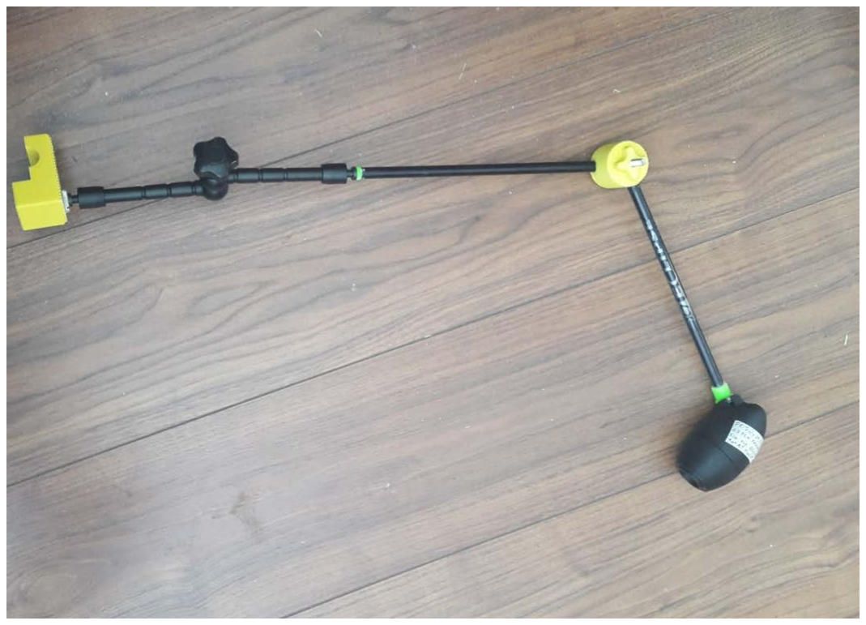
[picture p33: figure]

Figure 6 - From Left to Right: 3D Printed Clamp, Adapter, Articulating Arm, 3D Printed Adapter, Arrow Shaft, Disk Gear & Hand Knob, Arrow Shaft, 3D Printed Adapter, LipSync
Option 2
3D Printed Clamp + Nuts and Bolts | 1 | - | $3 | $3 1/4" Male To 3/8" Male Thread
| Adapter | 1 | Amazon | $7 | $7
| 3/8" Female to 5/8" Male thread adapter | 1 | Amazon | $7 | $7
MSA9030-19B | 19" Gooseneck, Black | 1 | Best Buy | $15 | $15
MSA9030-13B | 13" Gooseneck, Black | 1 | Best Buy | $10 | $10
| | | | TOTAL | $43

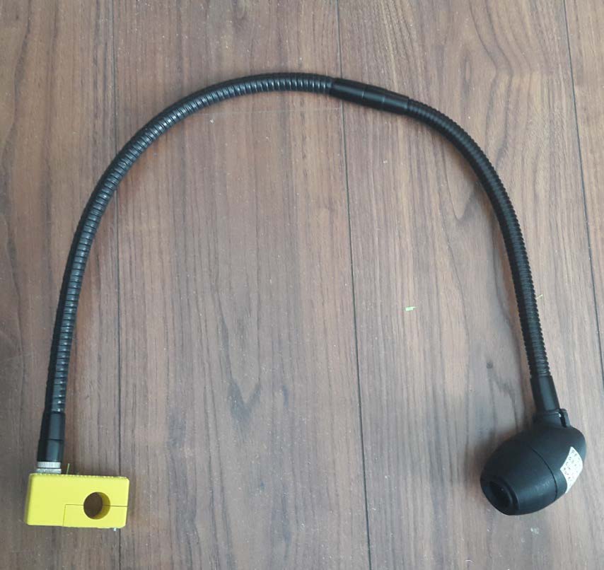
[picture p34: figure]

Figure 7 - From Left to Right: 3D Printed Clamp, Adapters, 19" Gooseneck, 13" Gooseneck, LipSync
Option 3
11" Articulating Magic Arm + Small Clamp Crab Pliers + Gopro Adapter+ Stainless Steel Thumber Screw Accessory Kit | 1 | Link Delight | $24 | $24
Female 1/4"-20 to 5/8"-27 Male 2 Piece Mic Adapter | 1 | Amazon | $9 | $9
19" Gooseneck, Black | 1 | Best Buy | $15 | $15
| | | TOTAL | $48
$50-$99
The options below increase in price due to the use of a commercial clamp (with the exception of option 2). The price is still otherwise competitive compared to other options due to the fact that the parts used are not necessarily meant for assistive technology applications. For instance as mentioned in the previous section (Suppliers), Loc Line was originally developed for cooling purposes for machine tool operations.
Part No. | Description | Qty | Supplier | Approximate Cost (CAD)

Total
Option 1
| Clamp with standard stud | 1 | Amazon | $28 | $28
MSA9030-19B | 19" Gooseneck, Black | 1 | Best Buy | $15 | $15
MSA9030-13B | 13" Gooseneck, Black | 1 | Best Buy | $10 | $10
| | | | TOTAL | $53

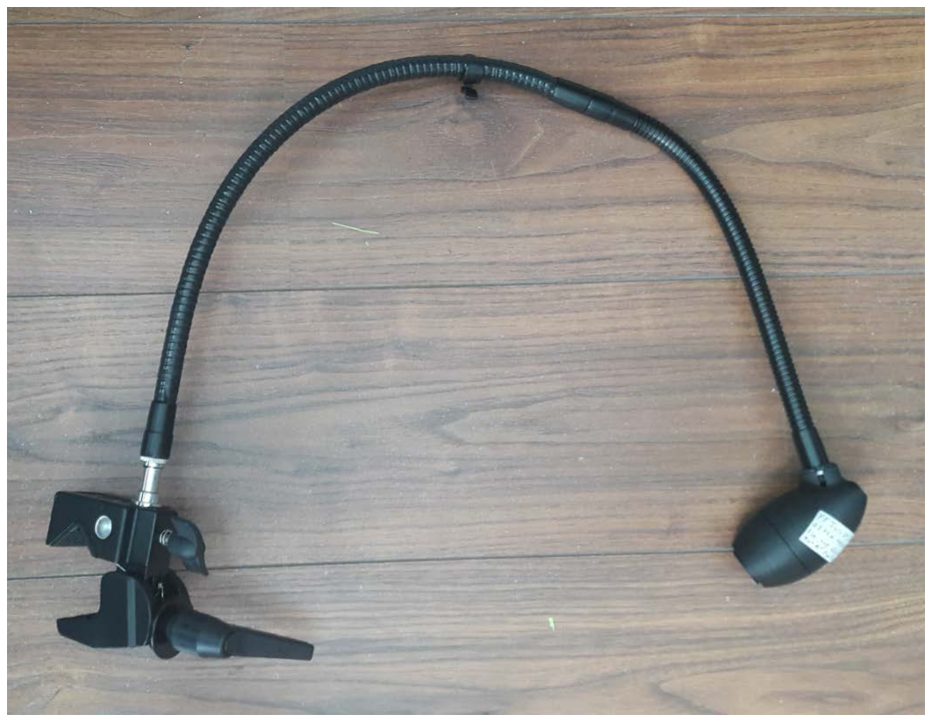
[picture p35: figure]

Figure 8 - From left to right: Super Clamp, Standard Stud, 19" Gooseneck, 13" Gooseneck, LipSync
Option 2
| 3D Printed Clamp+Nuts and Bolts | 1 | - | $3 | $3
| 1/4" Male To 3/8" Male Thread Adapter | 1 | Amazon | $7 | $7
| 3/8" Female to 5/8" Male thread adapter | 1 | Amazon | $7 | $7
MSA9505 | Posi-Lock Telescoping Mini-Boom | 1 | Amazon | $30 | $30
MSA9030-19B | 6" Gooseneck, Black | 1 | Best Buy | $7 | $7
| | | | TOTAL | $54

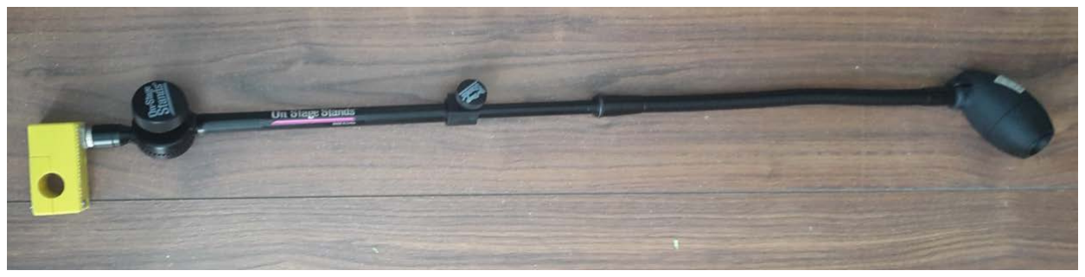
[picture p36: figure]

Figure 9 - From Left to Right: 3D Printed Clamp, Adapters, Posi-Lock Telescoping Mini-Boom, 13" Gooseneck, LipSync

Option 3
512001 | Round Tube and Flat Surface Clamp Kit. (see above) | 1 | Modular Hose | $39 | $39
61501 | Loc-Line Hose Segments Pack for 3/4" ID System. Includes (2) 5 3/4" segments. Approximately 1 foot. (see above) | 1 | EH Pope | $7 | $7
51801 | 1/2" Hose, one foot, in Black (51801-BLK) -1/2" Black Loc-Line | 1 | EH Pope | $6 | $6
61508 | 3/4" to 1/2" Adapter in Black (61508-BLK) -Black Hose | 1 | EH Pope | $3 | $3
51805 | 1/2" NPT Connector in Black (51805-BLK) -1/2" Black Loc-Line | 1 | EH Pope | $1 | $1
| | | | TOTAL | $56

Option 4
| Clamp with standard stud | 1 | | $28 | $28
MSA9505 | Posi-Lock Telescoping Mini-Boom | 1 | Amazon | $29 | $29
MSA9030-19B | 13" Gooseneck, Black | 1 | Best Buy | $10 | $10
| | | | TOTAL | $67

$100+
These assemblies are used in industries such as the assistive technology industry or the photography industry. Their robustness, weight capacity and industrial use drive their prices up.
Part No. | Description | Qty | Supplier | Approximate Cost (CAD)

Total
Option 1
035 | Super Clamp | 1 | Manfrot to | $57 | $57
237 HD | Heavy duty flex arm. ID 18mm. | 1 | Manfrot to | $50 | $50
| Female 1/4"-20 to 5/8"-27 Female Adapter | 1 | Amazon | $9 | $9
| | | | TOTAL | $116

Option 2
| Clamp with standard stud | 1 | Amazon | $28 | $28
244N | Variable friction arm | 1 | Manfrot to | $210 | $200
| 1/4" To 3/8" Thread Adapter | 1 | Amazon | $9 | $9
| 5/8" Male to 3/8" Female Microphone Mic Stand Adapter | 1 | Amazon | $3 | $3
| | | | TOTAL | $240

## Mobile Device

No Mount
In many cases, the mobile device may be placed on the users lap, the lap tray mounted on their wheelchair, or on a table in front of the user. In this case there is no need for a mount. A stand may be used to adjust the viewing angle of the phone.
Mount
Phone mounts have a standard 1/4"-20 female thread. Therefore any mobile device holder may be selected in combination with the LipSync mounting options listed in the previous section (LipSync). The changes that need to be made relate to adding an adapter with a 1/4"-20 male thread. One potential option for a phone mount assembly is listed in the table below.
Part No. | Description | Qty | Supplier | Approximate Cost (CAD) | Total
| Mudder Universal Smartphone Holder Mount Adapter for Monopod Tripod Selfie Stick with Double Screw Head, Black | 1 | Amazon | $13 | $13
| Thread Adapter Microphone Stand 5/8"-27 Female to 1/4"-20 Male for Camera Monitor | 1 | Amazon | $9 | $9
MSA9030-19B | 19" Gooseneck, Black | 1 | Best Buy | $15 | $15
| Clamp with standard stud | 1 | Amazon | $28 | $28
| | | | TOTAL | $65

Combining LipSync and Mobile Device
There are some options to combine both the LipSync and a mobile device into one mount assembly setup. The idea of combining the LipSync and a mobile device simplifies the mount assembly process since it requires choosing only one mounting point. Combining the two systems also allows for a reduction in price since only one clamp is used. Two possible combinations were assessed and will be detailed below.
The first option includes the Loc Line hoses. Since a Y fitting is available, a system using these hoses can be formed to attach both a mobile device and the LipSync. The table below provides a complete assembly.
Part No. | Description | Qty | Supplier | Approximate Cost (CAD) | Total
512001 | Round Tube and Flat Surface Clamp Kit. | 1 | Modular Hose | $39 | $39
61501 | Loc-Line Hose Segments Pack for 3/4" ID System. Includes (2) 5 3/4" segments. Approximately 1 foot. (see above) | 2 | EH Pope | $7 | $14
51801 | 1/2" Hose, one foot, in Black (51801-BLK) -1/2" Black Loc-Line | 1 | EH Pope | $6 | $6
61511 | Loc-Line Y Fitting for 3/4" ID System. | 2 | EH Pope | $4 | $4
61508 | 3/4" to 1/2" Adapter in Black (61508-BLK) -Black Hose | 1 | EH Pope | $3 | $3

570009 | Extra deep V-tabs for tabX tablet holder. | 1 | Modular Hose | $24 | $24
51805 | 1/2" NPT Connector in Black (51805-BLK) -1/2" Black Loc-Line | 1 | EH Pope | $1 | $1
| | | | TOTAL | $91

The second option was developed for using goosenecks. This option includes a 3D printed bracket with 2 holes for the goosenecks. The image below shows the bracket holding 1 gooseneck. The other hole is meant to support another gooseneck

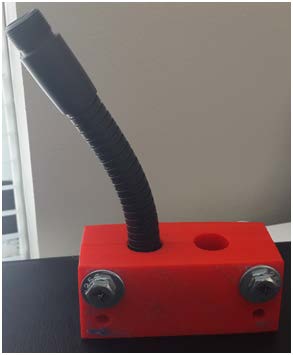
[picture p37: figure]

Figure 10 - 3D Printed Bracket Holding a Gooseneck
Part No. | Description | Qty | Supplier | Approximate Cost (CAD) | Total
| Clamp with standard stud | 1 | Amazon | $28 | $28
| 3D printed bracket | 1 | | $3 | $3
MSA9030-19B | 19" Gooseneck, Black 13" Gooseneck, Black | 2 1 | Best Buy Best Buy | $15 $10 | $30 MSA9030-13B $10 TOTAL $71

## Suggestions for Assembling Mounts

1. Tape some anti-skid pads like Dycem pads or "Magic Wrap" to increase the friction of the clamps and reduce their rotation about the tube.
2. If two assembly pieces are used, such as two goosenecks, glue them together at the attachment point to avoid separation or rotation.
3. Some of the problems associated with Loc-Line and goosenecks is the instability and their tendency to sag after continuous use. This could be solved using rescue tape, electrical tape or "Magic Wrap" wrapped around the pieces. Another solution is to add a stiff wire to the inside of the parts.
4. Goosenecks are a good option for small sections, but may become unstable as the length increases and may sag under their own weight. Therefore, it is not advisable to use goosenecks when the mounting point is further away from the user, such as the back of the wheelchair.
5. When using Loc Line, use the 3/4" tubes as the base to provide stability and stiffness to the setup. 1/2" tubes may be used at the top of the assembly.

### Appendix A Checklist for After Choosing a Mount

☐ Is the clamp secure and does not move?
☐ With the mount attached is there clearance around the wheels/wires/chair frame? ☐ Does the wheelchair fit through doorways?
☐ Is it possible for the mount to be snagged on obstructions as the user drives around? ☐ Is the driving view of the user clear with no obstructions?
☐ Is the mobile device within viewing angle of the LipSync?
☐ Can the user easily reach the LipSync to use it?

### Appendix B Assembly Instructions for 3D Printed Clamp

Tools:
1. Screwdriver
2. Glue
Components:
1. (4) 6-32x1" Round Head Machine Screws
2. (4) 6-32 Hex Machine Nuts
3. 3D Printed Clamp
4. 2" Piece of Magic Wrap
5. (1) Female 1/4"-20 to 5/8"-27 Male 2 Piece Mic Adapter
Steps:
1. Glue the 4 nuts in their assigned slots on the bottom piece of the clamp. Make sure not to add too much glue to avoid blocking the hole.

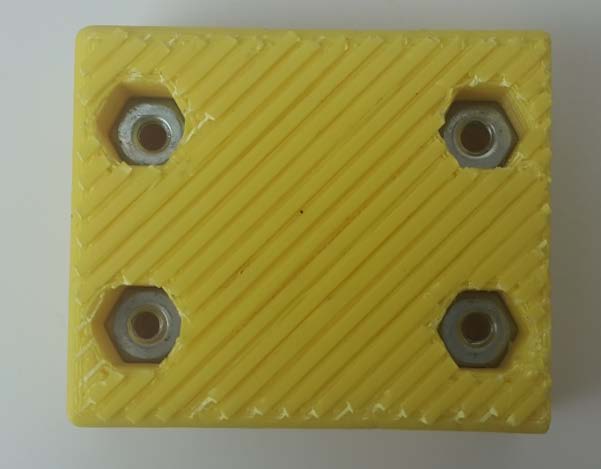
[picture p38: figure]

Figure 11 - Glued Nuts in Bottom Piece of Clamp
2. Glue the Female 1/4"-20 to 5/8"-27 Male 2 Piece Mic Adapter into the hole in the assembled 3D printed clamp as shown in the image below.

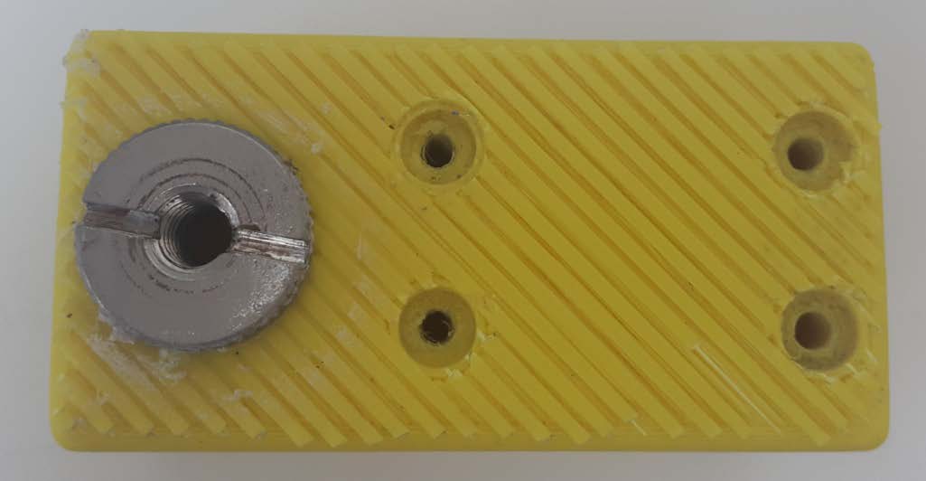
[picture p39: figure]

Figure 12 - Glued 1/4"-20 to 5/8"-27 Adapter in 3D Printed Clamp
3. Wrap the 2" piece of Magic Wrap around the section of the tube that you plan on mounting in to.

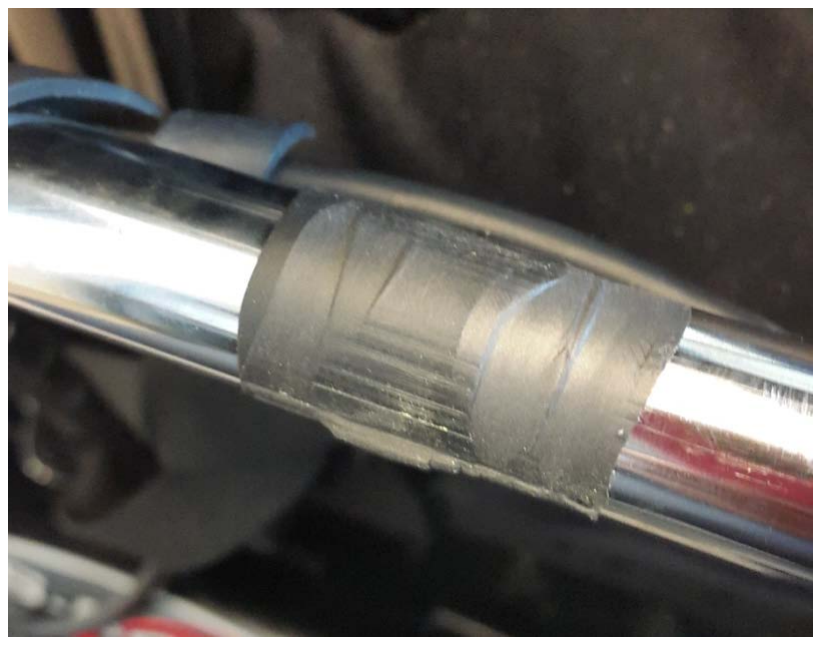
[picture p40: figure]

Figure 13 - Magic Wrap Around Wheelchair Tube
4. Place the bottom piece of the clamp on the Magic Wrap.
5. Align the top piece with the bottom piece and screw in the first bolt until it is secure. Repeat for the other 3 bolts.

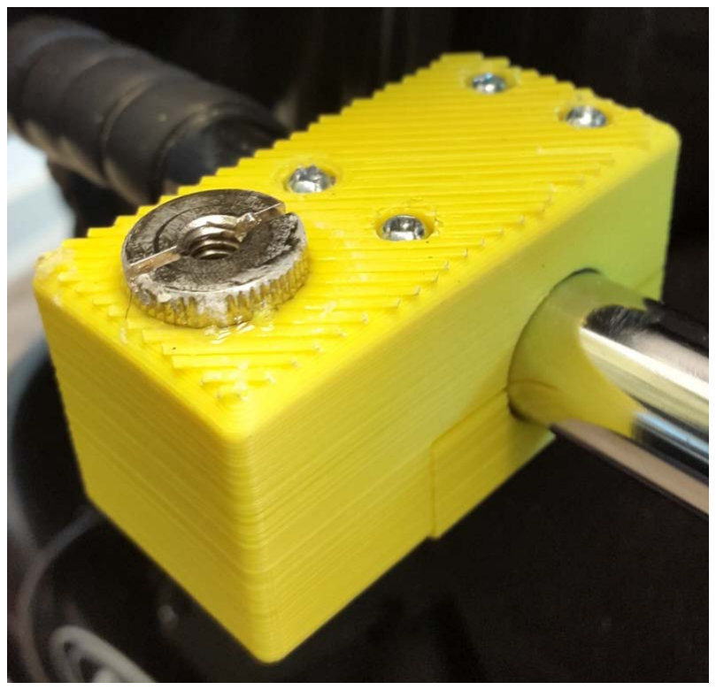
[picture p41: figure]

Figure 14 - Complete Assembly of Clamp

### Appendix C Assembly Instructions for DIY Mount

Tools:
1. Glue
2. Tube Cutter or Saw
Components:
1. (1) 5/16 in.-24 tpi x 1-1/2 in. Hex Cap Screw
2. (1) 5/16 in. Nut
3. 3D Printed Clamp
4. 3D Printed Disk Gear & Hand Knob
5. 3D Printed Threaded Adapters: 1/4-20 threaded insert & 3/8-16 threaded holder
6. 11" Inch Friction Articulating Magic Arm for Camera DSLR
7. Arrow Shaft - for the models provided we used an Easton Eclipse 2512 Arrow Shaft For the second possible assembly:
8. Mini Ball Head with Lock and Hot Shoe Adapter Camera (optional)
9. 1/4 male to 3/8 male adapter (optional)
10. 3/8 female to 5/8 male adapter (optiona)
Steps:
1. Assemble the 3D printed clamp as described in Appendix B Assembly Instructions for 3D Printed Clamp.

2. Screw the 11" Inch Friction Articulating Magic Arm for Camera DSLR into the Mic Adapter in the 3D printed clamp.
3. Determine the length of the arrow shaft necessary by adjusting the articulating arm and approximating the length necessary to reach the mouth of the user. There will be two sections of arrow shafts in total.
4. Use the tube cutter to cut the arrow shaft to size. Make sure to file the ends of the arrow shaft to remove sharp edges.
Note: we found that increasing the length of the arrow shaft increases the vibration of the whole assembly, which makes it difficult to use the LipSync. The maximum suggested length arrow shaft to use is 9".
5. Glue the 3D printed 3/8-16 threaded holder on one end of an arrow shaft.
6. Screw in the 5/8 to 3/8 threaded adapter in the LipSync. Make sure to leave room for the LipSync spacer or to place the spacer in its position.
7. Screw the 3/8-16 threaded holder into LipSync to help with aligning the Disk Gear. Be careful not to over-tighten as to avoid breaking the threaded holder.
8. Place the Disk Gear at the other end of the arrow shaft. Make sure that the side of the disk is aligned with the LipSync as shown in the image below. Glue the arrow shaft in the Disk Gear.

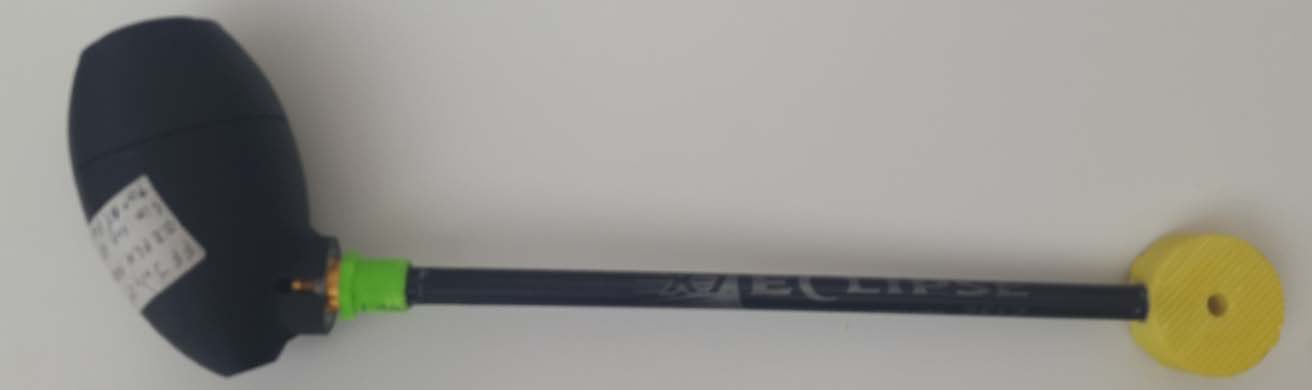
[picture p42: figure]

Figure 15 - Disk Gear Aligned with the LipSync

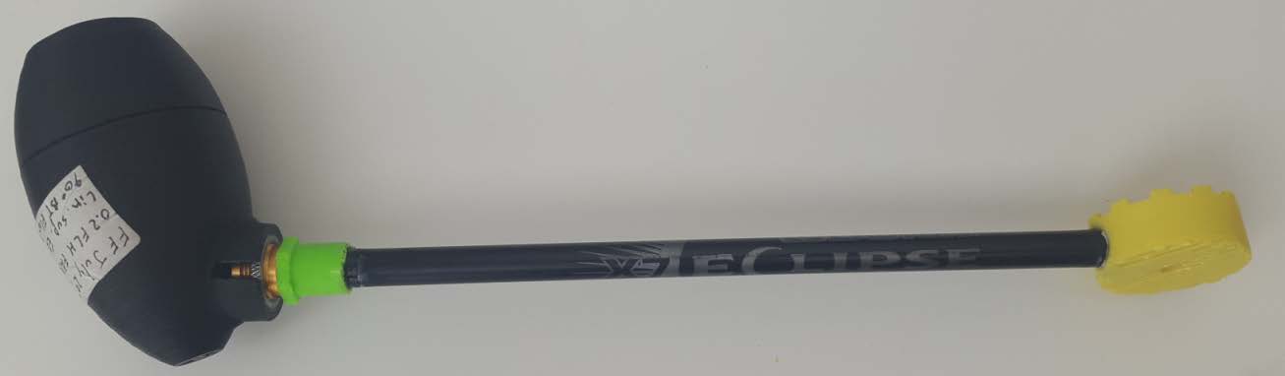
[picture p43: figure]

Figure 16 - Misaligned Disk Gear
9. Grab the other arrow shaft and glue the 3D printed 1/4-20 threaded insert.
10. Place the Disk Gear at the other end of the arrow shaft and glue it in place.
11. Place the Articulating Magic Arm onto the arrow shaft with the 1/4-20 threaded insert by threading it into the arrow shaft. It is advisable to glue the 1/4-20 insert to the Articulating Magic Arm to provide stability to the assembly.
12. Glue the 5/16 in nut int the 3D printed hand knob.

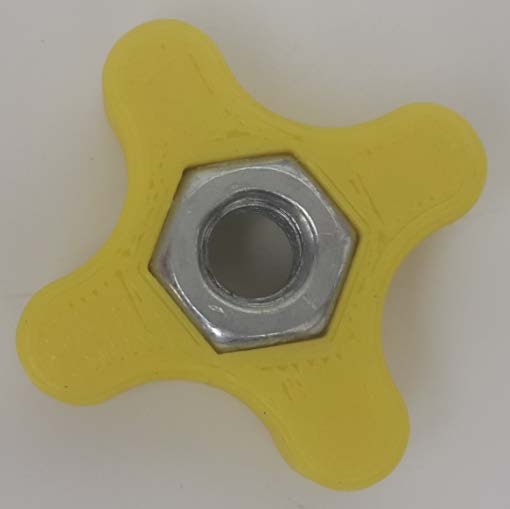
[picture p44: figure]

Figure 17 - Glued Nut in 3D Printed Hand Knob
13. Attach the second arrow shaft to the first by meshing the Disk Gear together. Use the 5/16 in.-24 tpi x 1-1/2 in. Hex Cap Screw and the Hand Knob to tighten the disk. You can glue in the Hex Cap Screw to keep it in place.

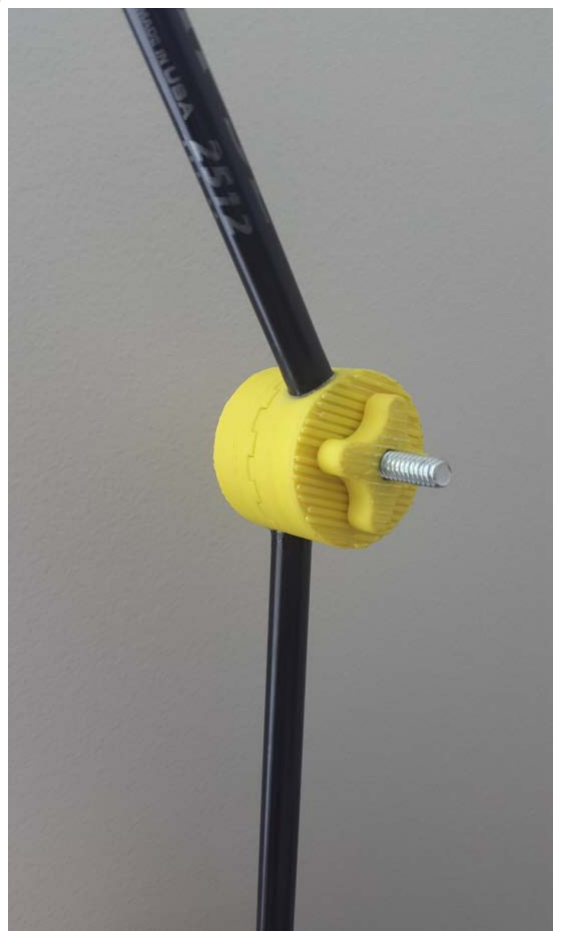
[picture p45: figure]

Figure 18 - Disk Gear Used to Adjust the Angle of the Arrow Shafts
14. Use both the Disk Gear and the Articulating Arm to adjust the angle of the LipSync.

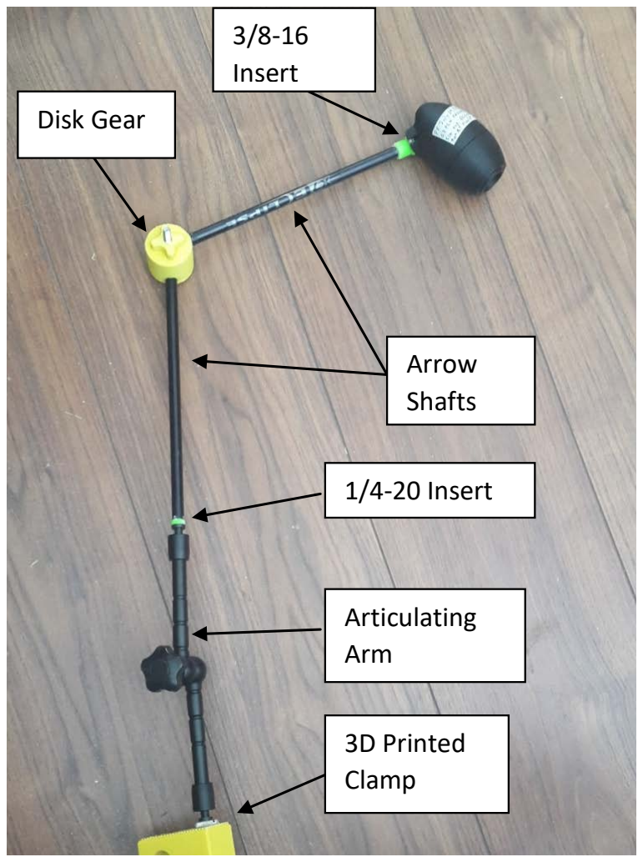
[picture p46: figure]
3D Printed Clamp; Articulating Arm; 1/4-20 Insert; Arrow Shafts; Disk Gear; 3/8-16 Insert

For the optional component:
15. Follow steps 1-4 outlined above.
16. Glue in the 3D printed 1/4-20 threaded insert on one end of an arrow shaft.
17. Glue in the bottom piece of the Disk Gear at the other end of the arrow shaft.
18. Grab the other arrow shaft and repeat step 2.
19. Glue the top piece of the Disk Gear at the other end of the arrow shaft.
20. Place the Mini Ball Head with Lock onto the other arrow shaft with the 1/4-20 threaded insert by threading it into the insert. It is advisable to glue the 1/4-20 insert to the Mini Ball Head with Lock to provide stability to the assembly.
21. Thread the 3/8 female to 5/8 male into the LipSync. Thread the 1/4 male to 3/8 male adapter into the adapter in the LipSync.
22. Thread the Mini Ball Head into the LipSync and adapter assembly.
23. Follow steps 12-13 outlined above.
24. Use the Disk Gear, Articulating Arm, and the Mini Ball Head to adjust the angle of the LipSync.

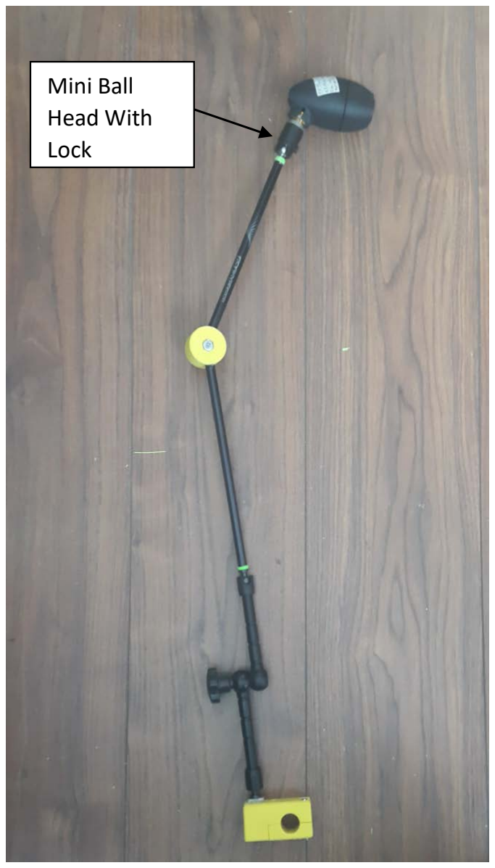
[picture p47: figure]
Mini Ball Head With Lock

Figure 19 - Complete Assembly of DIY Mount With Mini Ball Head

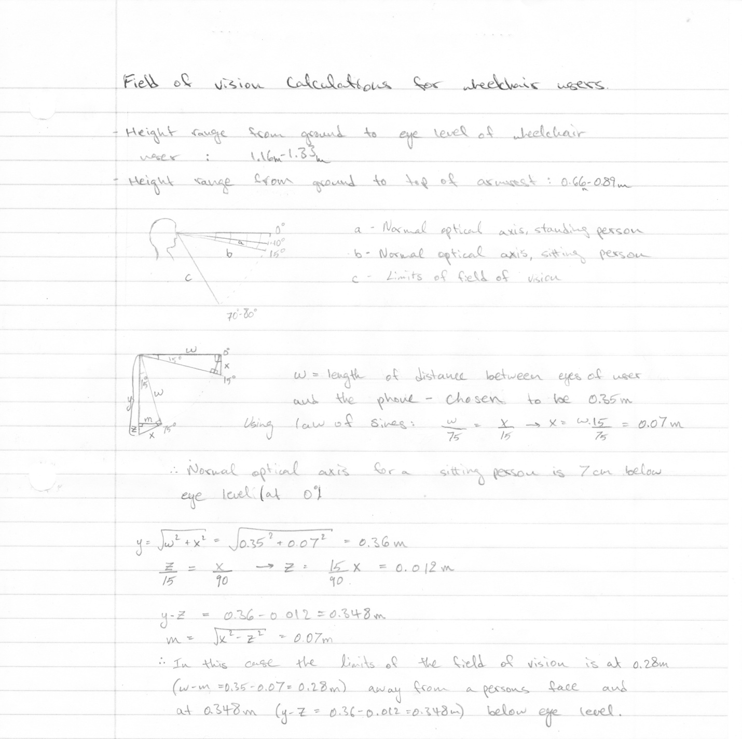
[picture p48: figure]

### Appendix D Field of Vision Claculations

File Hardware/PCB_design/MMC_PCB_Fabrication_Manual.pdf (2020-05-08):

# MMC PCB Fabrication Manual

Version 1.0
2020/05/05

Makers Making Change
PCB Fabrication Manual | PCB Fabrication Manual
Version 1.0 | Page 2 of 10

## Table of Contents

## 1. Introduction

## 1.1. What is PCB?

PCB (Printed circuit board) is a board that has lines and pads that connect various points together. The board includes traces that electrically connect the various connectors and components to each other. A PCB allows signals and power to be routed between physical devices. Solder is the metal that makes the electrical connections between the surface of the PCB and the electronic components. [1]

## 1.2. What is PCB Fabrication?

PCB fabrication is the assembly method for circuit boards used in electronic devices. The layers of the board are put together along with the specific surface pattern based on the design files that is used in electronics manufacturing.[2]

## 1.3. What is gerber file?

Users create their own files for manufacturing based on the design files and send them to the manufacturer. The design files for manufacturing PCB is converted to a standard format known as a Gerber file. This is an industry standard for recording the specification of a PCB.[2]

## 2. PCB design tools

There are many different tools for designing PCB’s and you can select any of the available tools based on your previous experience or the requirements of your design. The process of designing PCB is not in the scope of this document but you can find courses or books that can help you understand the process of designing electronics circuits and PCB’s.

Here are the most common PCB design tools:

- Altium Designer (https://www.altium.com/) : Paid with Free Trial and student license.
- Eagle (https://www.autodesk.ca/en/products/eagle/) : Free limited version includes 2 schematic sheets, 2 signal layers, and an 80cm2 (12.4in2) board area.
- Kicad (https://www.kicad-pcb.org/) : Opensource with GNU’s GPL copyright agreement.
- Fritzing (https://fritzing.org/) : Opensource version available on github and the paid application is available. Limited options suitable for basic designs.
- Upverter (https://upverter.com/) : Free cloud-based design tool. It requires sign up for usage.

There are other available tools that can be used to design PCBs.

## 3. How to generate PCB gerber files for fabrication?

Once the PCB board file is created using your favorite PCB design tool then you can generate gerber files which is used by PCB fabrication companies to fabricate your design. The CAM processing tool uses the gerber generator file to create gerber files. The gerber generator file is usually provided by PCB fabrication company of your choice or can be created based on gerber files format which can be found on the website of the PCB fabrication company.

Each PCB board file includes different top and bottom layers and gerber files provide specifications for each of these layers by combining layers together based on the format specified by gerber file generator.

Common layers:

- Top & Bottom Copper
- Top & Bottom Silkscreen
- Top & Bottom Soldermask
- Drill
- Drill Station Info
- Photoplotter Info
- Mill Layer
- Top Paste

There is no standard format for the gerber file generator and there are variations of formats used by PCB fabrication companies.

You can find the final generated gerber files of the projects involving PCB designs for common PCB fabrication companies on our website. You can use the generated gerber files available if you are using one of the fabrication companies listed below or you can create your own gerber files based on PCB design files.

- Seeed Fusion PCB (https://www.seeedstudio.com/fusion.html)
- PCBWay (https://www.pcbway.com/)
- OSH Park ~ (https://oshpark.com/)
- JLCPCB (https://jlcpcb.com/)

We now go over process of generating gerber files using three common PCB design tools.

## Eagle

1. Open the board file of your PCB design using Eagle
2. Select File > CAM Processor
3. Click on “Load job file” dropdown menu button and select “Open CAM file”
4. Download or create the gerber generator file (.cam) used by your PCB fabrication company of your choice
5. Navigate in your system and find the directory that includes the gerber file generator file with. cam extension
6. Select the gerber file generator file and click on “Open” button
7. Double check the Output file layers on left menu bar to make sure there are no layers are missing
8. Click on “Process Job” button
9. Select the output directory (Create a new directory called “gerbers” as an example)
10. The process of creating the gerber file will start and finish once you receive a popup message indicating that “Job Proceed Successfully!”
11. Click on “OK” button
12. Navigate to the directory that includes the generated gerber files (“gerbers” directory as an example)
13. Select all the gerber/drill files in the directory that saved them and generate a compressed file in Zip format.
14. You can now submit the compressed Zip file that includes the gerber files to the PCB fabrication company of your choice.

## Altium designer

1. Open the board file of your .PCB design file using Altium designer. [3]
2. Select File > Fabrication Outputs > Gerber Files
3. Select General setting in Gerber Setup window
4. Set the units in “inches” precision to “2:5” in General setting
5. Select Layers setting in Gerber Setup window
6. Next, make sure you have the clear outline in mechanical layer.

7. Check the layers in “Plot” column under “Layers To Plot” section for creating gerber files according to fabrication company instructions.
- Check following layers: GTO, GTP, GTS, GTL, GBL , GBS , GBP , GBO , GKO ,GPT , GPB , GM(Number)
- There will be no middle layer if you PCB board includes only 2-layers. All our design files include 2 layers which means you need to uncheck all middle layers (G1,G2,G3....)
- You can use the “Plot Layer” option and select the “Used On” to automatically check the used layers in your design.
8. Select “All Off” in “Mirror Layers” or uncheck every layer in “Mirror Layers” column
9. Uncheck all the layers in the plot column of “Mechanical Layers to Add to All Gerber Plots”
10. Check “Embedded apertures (RS274X)” under “Aperture” setting
11. Click on the “OK” button to generate gerber files.
12. Gerber files are automatically loaded in the Altium cam viewer. You can use “CAMtastic” view to verify that all layers have been generated correctly.
13. The gerber files should now be generated and saved in directory of your project.
14. You can also export gerber files to a new directory using following steps:
- Select File > Export > Gerber…
- Click on “OK”
- Select the path to the directory that you would like to save all the gerber files. (“gerbers” directory as example)
- Click on “OK” to export all the gerber files
15. Next, Generate the Drilling layer in Excellon format
16. Select File > Fabrication Outputs > NC Drill Files
17. Set the units in “inches” precision to “2:5” in NC Drill Setup window
18. Click on the “OK” button to generate drill files
19. The drill file should now be generated and saved as .TXT file in directory of your project.
20. You can also export file to a new directory using following steps:
- Select File > Export > Save Drill…
- Click on “OK”
- Select the path to the directory that you would like to save the drill file. (“gerbers” directory as example)
- Click on “OK” to export the drill file
21. Select the “Projects” view and highlight the “CAMtastic” cam file
22. Click on “Save As” under “File” and save the “CAMtastic” cam file.
23. Click on “Save”.
24. Select all the gerber/drill files in the directory that saved them and generate a compressed file in Zip format.

25. You can now submit the compressed Zip file that includes the gerber files to the PCB fabrication company of your choice.

## Kicad

1. Open the board file of your design file using Kicad. [4]
2. Select File > Plot
3. Check the layers in “Plot” window for creating gerber files according to fabrication company instructions.
- Check following layers: Top Copper (F.Cu), Soldermask (F.Mask), Silkscreen (F.SilkS), Bottom Copper (B.Cu), Soldermask (B.Mask), Silkscreen (B.SilkS), Board outline (Edge.Cuts)
4. Set the “Output directory” to save the generated gerber files. You can also use “Browse…” button to set the path to the directory.
5. Uncheck “Plot sheet reference on all layers” option.
6. Uncheck “Plot footprint values” option.
7. Check “Exclude PCB edge layer from other layers” option.
8. Check “Use Protel filename extensions” option.
9. Click on “Plot” button to generate and save gerber files in the specified output directory to save gerber files.
10. Next, configure the settings to generate drill file
11. Click on “Generate Drill File” button.
12. Set the “Output directory” to save the generated drill file. You can also use “Browse…” button to set the path to the directory. Use the same output directory as you selected to save the gerber files.
13. Check “Inches” as drill units.
14. Check “Decimal Format” as zeros format.
15. Check “PostScript” as drill map file format.
16. Check the “Merge PTH and NPTH holes into one file” option
17. Click on “Drill File” or press “Enter” to generate the drill file.
18. Click on “Close” to close “Drill Files Generation” Window.
19. Click on “Close” again to close “Plot” Window.
20. Verify the generated gerber files using a gerber viewer tool to make sure that all layers have been generated correctly.
21. Select all the gerber/drill files in the directory that saved them and generate a compressed file in Zip format.
22. You can now submit the compressed Zip file that includes the gerber files to the PCB fabrication company of your choice.

## 4. How to check and confirm PCB gerber files?

It is recommended to double check or triple check the final generated gerber files of your design to make sure there are no issues with process of gerber files generation. The PCB fabrication companies mostly provide online gerber file viewer tools that you can use to confirm your design once you upload your gerber files compressed as a Zip file. However, you can use other gerber file viewer to check your design files before submitting the gerber files.

The following gerber viewer tools are recommended:

- Online Gerber Viewer (https://www.gerber-viewer.com/)
- gerbv (https://sourceforge.net/projects/gerbv/)

Select all the generated gerber file layers in the “gerbers” directory and view them to make sure all the layers are aligned.

## 5. Where to send PCB gerber files for fabrication?

The process to send the gerber files for fabrication may differ from company to company but there are general steps you can follow to send your gerber files for fabrication.

1. Select the fabrication company (Here are our recommended fabrication companies)
- Seeed Fusion PCB
- PCBWay
- OSH Park ~
- JLCPCB
2. Create an account on PCB fabrication website or use temporary login if it is available
3. Select the fabrication service
4. Upload the compressed Zip file that includes your gerber files
5. Select the available options based on your design requirements. The standard options for most of our projects:
- PCB Layers: 2 Layers
- PCB dimensions should update based on your uploaded gerber files, but you can manually entry the dimensions as well
- PCB quantity can vary based on your requirements (Minimum 5)
- PCB Color can be changed if the fabrication company offers the option. The defualt option has the fastest turnaround time.
- Surface Finish: HASL
- Copper Weight, Minimum Drill Hole Size, Trace Width , Minimum Solder Mask Dam doesn’t require to be changed and the default value works
6. Check the uploaded gerber files using online gerber viewer tool if it is offered by the fabrication company and make sure there are no issues.

7. Add the uploaded design to the order
8. Add another design if you are doing multiple orders
9. Proceed to the checkout and enter your billing and shipment information
10. Select the shipping method
11. Submit your order for production
12. The technician will contact you for additional information or corrected files if there are issues with your design files.
13. You will receive an email when your design goes to production
14. You will receive another email once your PCBs are produced and shipped

This includes the instructions for fabrication of PCB designs based on generated gerber files.

## Reference

1. https://learn.sparkfun.com/tutorials/pcb-basics/all
2. https://www.hi5electronics.co.uk/what-is-pcb-fabrication/
3. https://support.jlcpcb.com/article/42-how-to-export-altium-pcb-to-gerber-files
4. https://support.jlcpcb.com/article/44-how-to-export-kicad-pcb-to-gerber-files

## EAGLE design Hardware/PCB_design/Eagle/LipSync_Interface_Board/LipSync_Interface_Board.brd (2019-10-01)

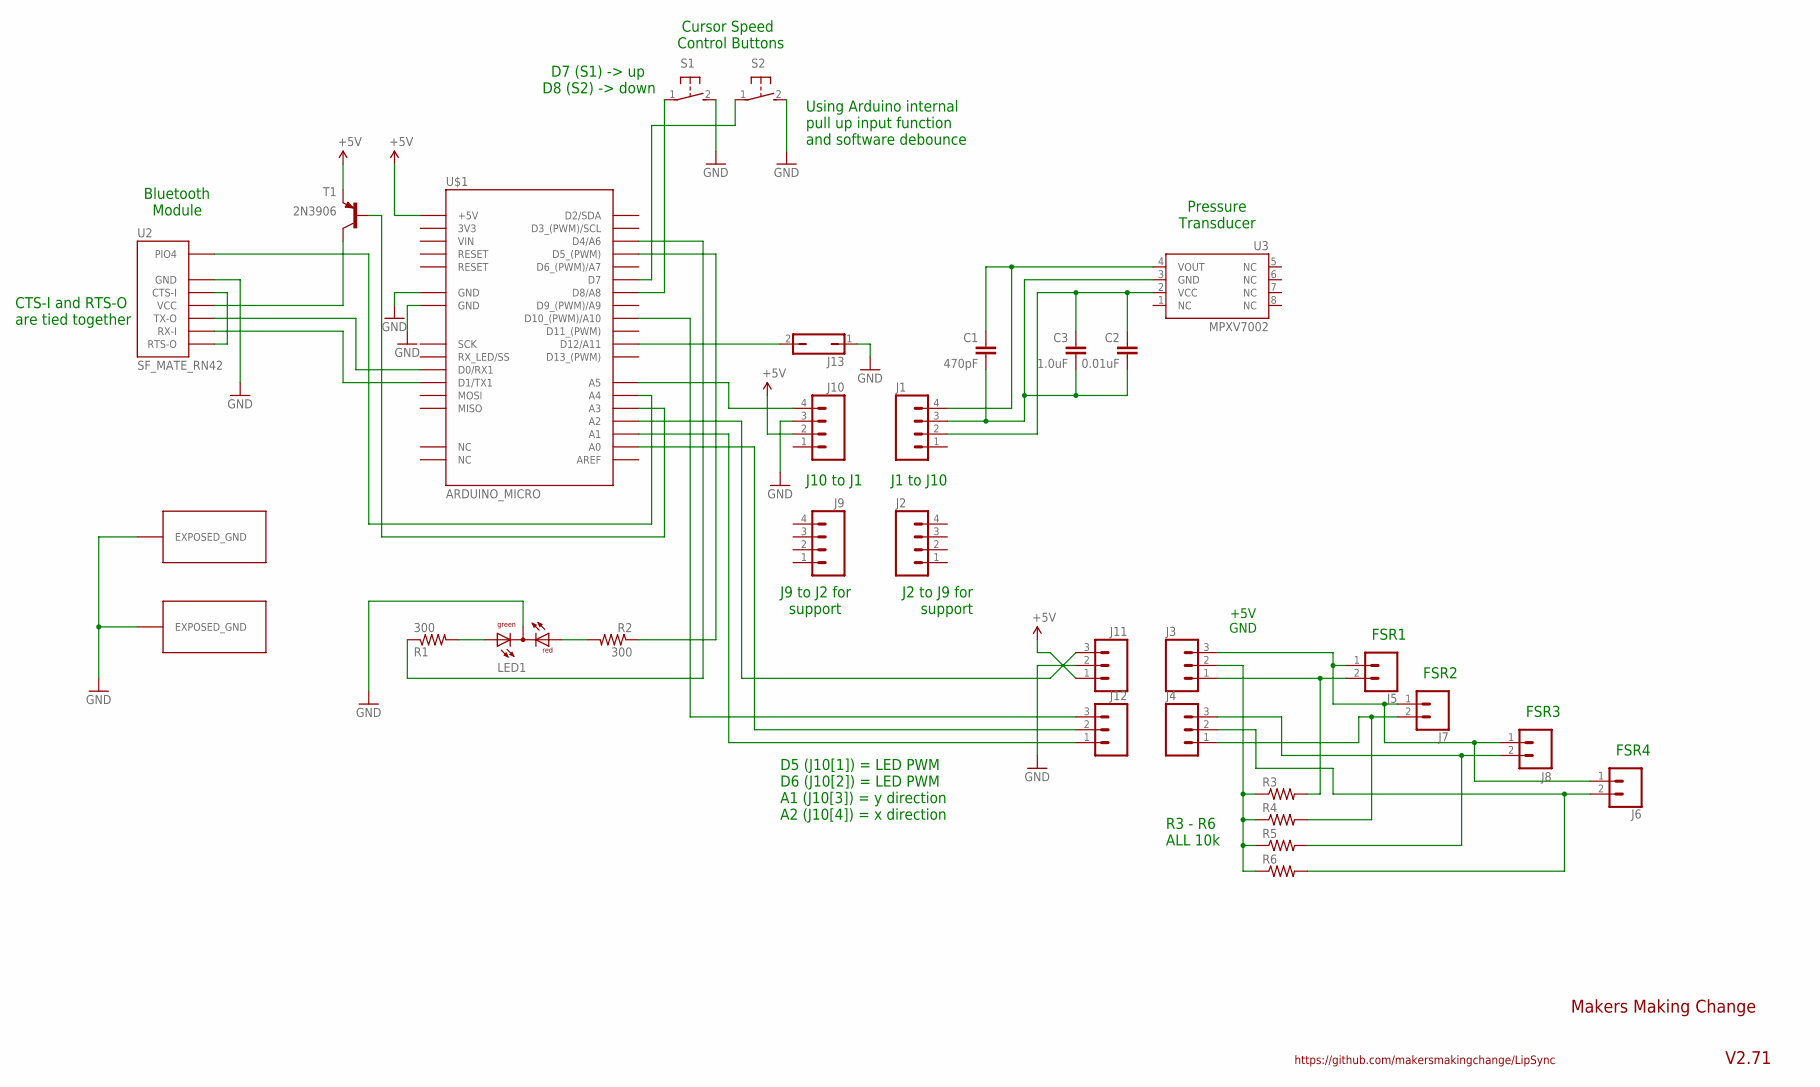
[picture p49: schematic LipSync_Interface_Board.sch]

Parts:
C1: 470pF; CAP-PTH-SMALLEZ
C2: 0.01uF; CAP-PTH-SMALLEZ
C3: 1.0uF; CAP-PTH-SMALLEZ
J1, J2, J9, J10: M04PTH; 1X04
J3, J4, J11, J12: M03LOCK; 1X03_LOCK
J5, J6, J7: CONN_02PTH3; 1X02_LONGPADS
J8: M02PTH3; 1X02_LONGPADS@1
J13: JP1Q; JP1
LED1: DUOLED-RG-C; DUOLED-C-5MM
R1, R2: 300; AXIAL-0.3
R3, R4, R5, R6: R-US_0204/5; 0204/5
S1, S2: 31-XXB3F-31XX-CUSTOM; B3F-31XX-CUSTOM
T1: 2N3906; TO92-EBC
U2: SF_MATE_RN42; BLUE_MATE_RN42_HEADER_FOOTPRINT
U3: MPXV7002; SOP8
U$1: ARDUINO_MICRO; ARDUINO_MICRO_HEADER_FOOTPRINT
U$2, U$3: EXPOSED_GND

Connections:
3V3: U$1.3V3
GND: J10.3, J11.2, J13.1, LED1.C, S1.2 (S), S2.2 (S), U2.GND, U$1.GND, U$1.GND@1 (GND), U$2.GND1, U$3.GND1
GND2: C1.2, C2.2, C3.2, J1.3, U3.3 (GND)
GND3: J3.2, R3.1, R4.1, R5.1, R6.1
unnamed: U2.PIO4, U$1.A4
unnamed: T1.C, U2.VCC
unnamed: U2.TX-O, U$1.RX1 (D0/RX1)
unnamed: U2.RX-I, U$1.TX1 (D1/TX1)
unnamed: J12.2, U$1.A0
unnamed: J12.1, U$1.A1
unnamed: C1.1, J1.4, U3.4 (VOUT)
unnamed: C2.1, C3.1, J1.2, U3.2 (VCC)
unnamed: U2.CTS-I, U2.RTS-O
unnamed: J12.3, U$1.D10 (D10_(PWM)/A10)
unnamed: J10.4, U$1.A5
unnamed: LED1.AX (AG), R1.P$2 (2)
unnamed: LED1.AR, R2.P$2 (2)
unnamed: S1.1, U$1.D8 (D8/A8)
unnamed: S2.1, U$1.D7
unnamed: J3.3, J5.1, J6.1, J7.1, J8.1
unnamed: R1.P$1 (1), U$1.D4 (D4/A6)
unnamed: R2.P$1 (1), U$1.D5 (D5_(PWM))
unnamed: T1.B, U$1.A3
unnamed: J11.3, U$1.A2
unnamed: J3.1, J5.2, R3.2
unnamed: J13.2, U$1.D12 (D12/A11)
unnamed: J4.1, J7.2, R4.2
unnamed: J4.3, J8.2, R5.2
unnamed: J4.2, J6.2, R6.2
VCC: J10.2, J11.1, T1.E, U$1.5V (+5V)

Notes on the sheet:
J9 to J2 for support
J2 to J9 for support
D5 (J10[1]) = LED PWM D6 (J10[2]) = LED PWM A1 (J10[3]) = y direction A2 (J10[4]) = x direction
CTS-I and RTS-O are tied together
J1 to J10
J10 to J1
Cursor Speed Control Buttons
D7 (S1) -> up D8 (S2) -> down
+5V GND
Bluetooth Module
Pressure Transducer
Using Arduino internal pull up input function and software debounce
R3 - R6 ALL 10k
FSR1
FSR2
FSR3
FSR4
Makers Making Change
V2.71
https://github.com/makersmakingchange/LipSync

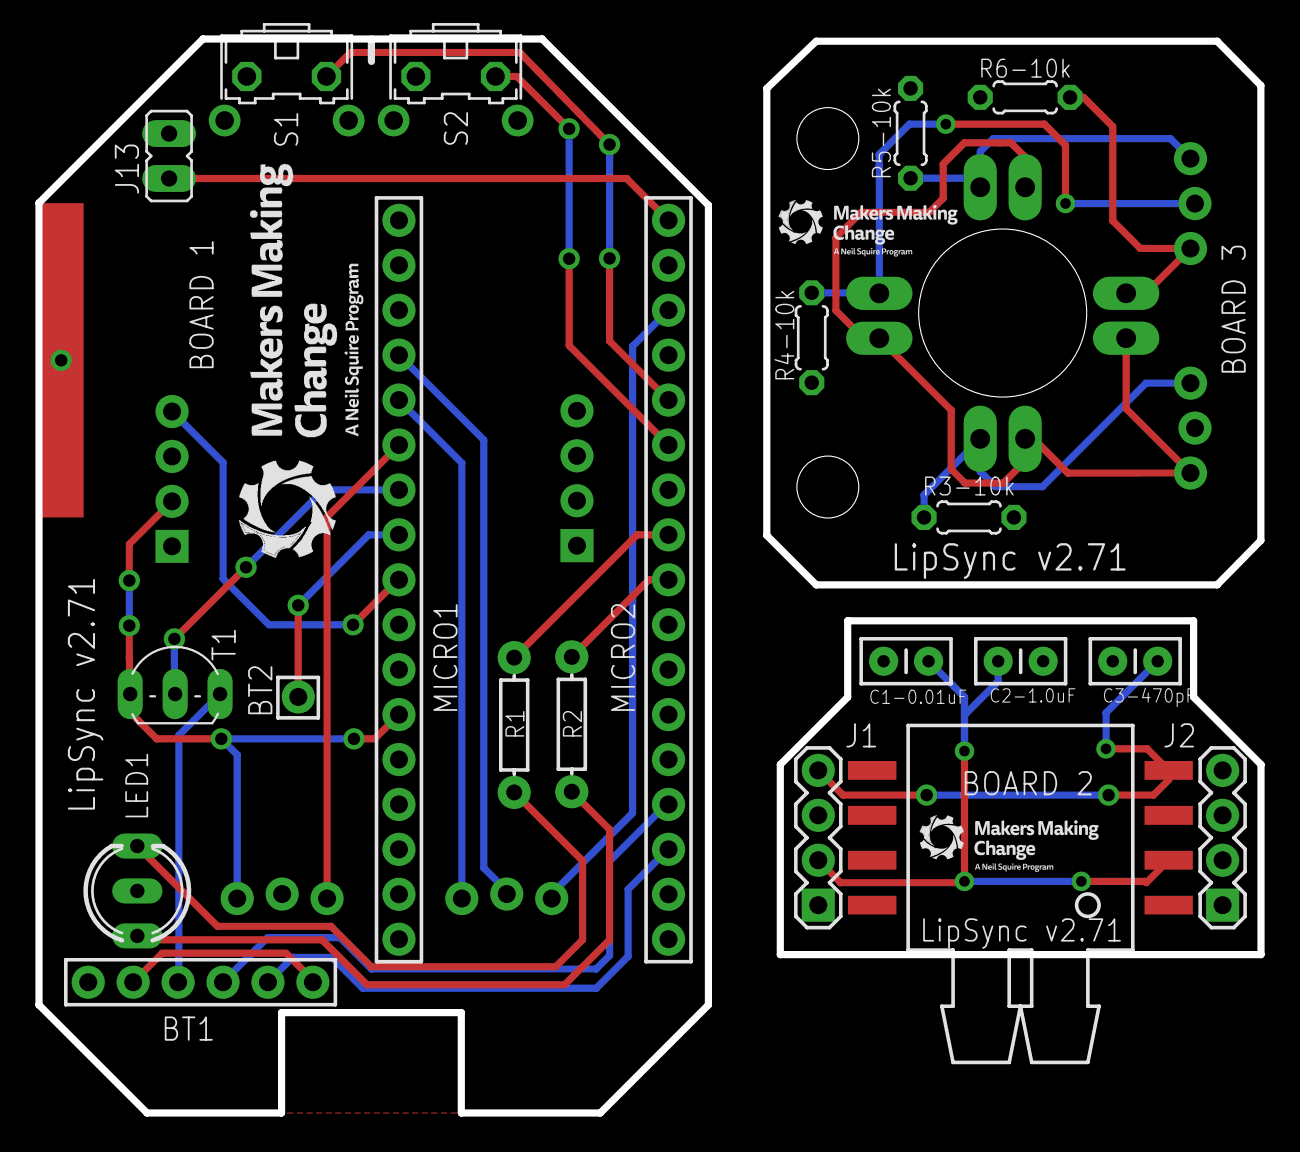
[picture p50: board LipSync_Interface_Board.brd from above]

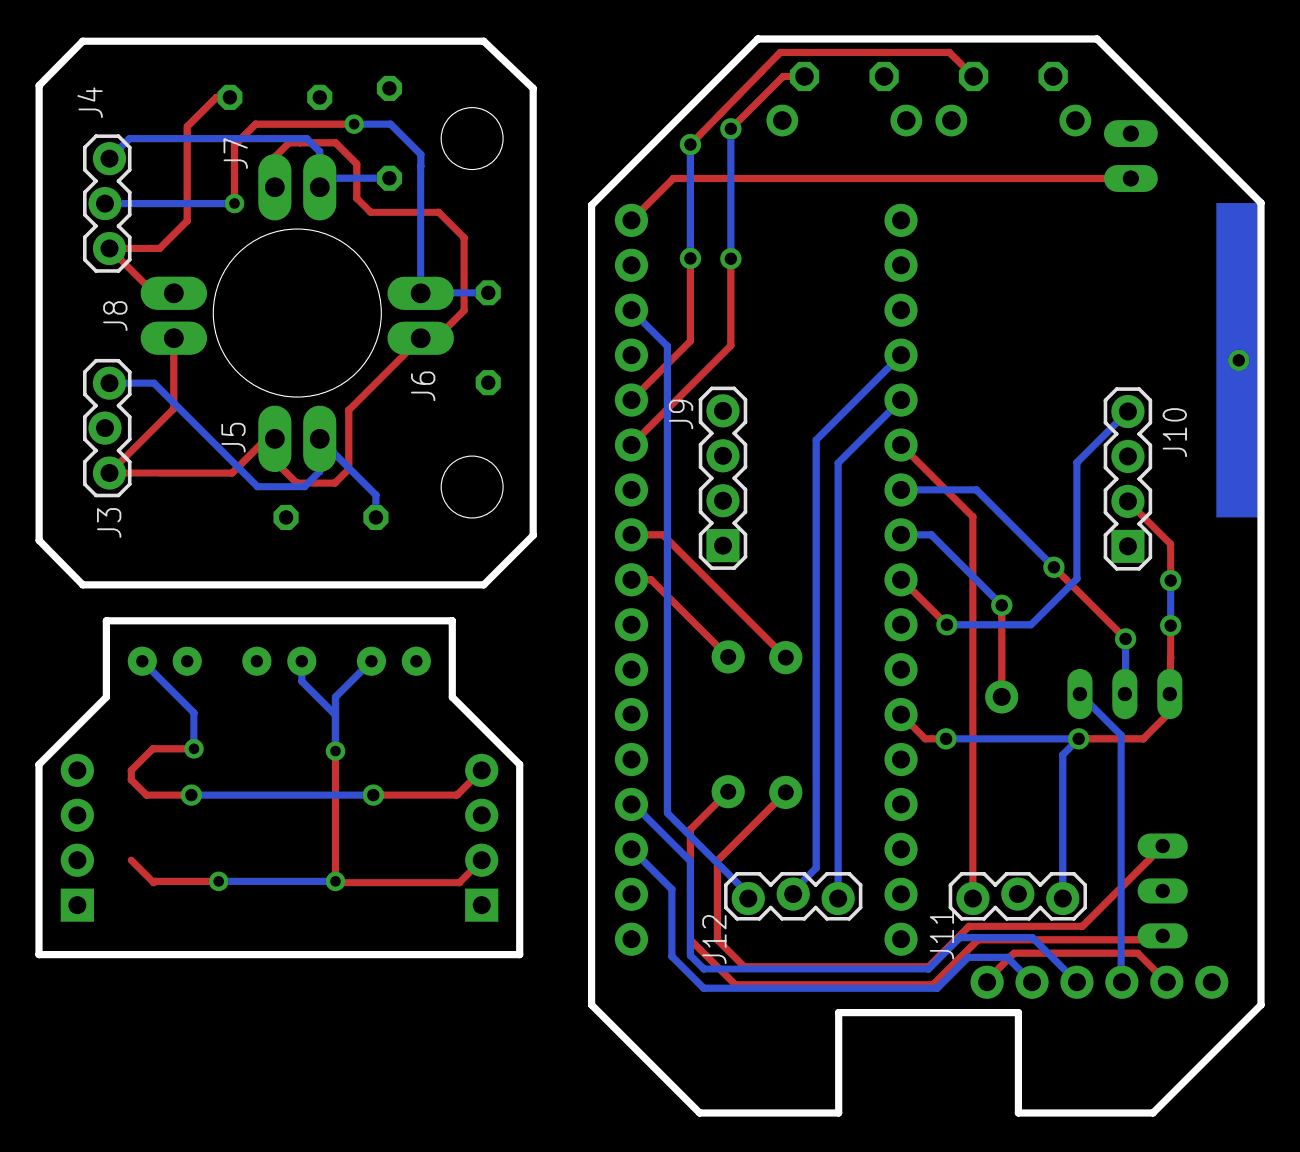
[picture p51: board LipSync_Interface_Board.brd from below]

Board: 2 copper layers, 69.1 x 60.7 mm, 31 parts (11 on the bottom side), 29 nets.

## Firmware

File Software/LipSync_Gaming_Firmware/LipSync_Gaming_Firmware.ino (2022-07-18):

/*
  *                 `.:/++`             ....``
  *              `/ossss: `.`         `--------.`
  *               /ssso. .----..```..-----------                                                                                                                                  ``
  *               -ss+``-----------------------.                  ssss       -/++/`              /ss-                                     ./++/-      //+//             oss       `oss-
  *              `os+ `----------------.......--`                 sssss:    `s400s.              +sH-                                     -sBsss`    :ssBCs             sVs        /++`
  *    ``      .:ss+ `-------..```````````````````                sso+ss`   +so/ss.   -:::::.    +se-  `---  `-::::.  `-:`.::. .::::-     -su/ss+   `ss:sss  `-::::-`   s5s   .--. ---  .-- -:::-    .::::---.
  *   .oso+++oossso``---..``          ``..----------.....--.      sso.ss/  -ss-/ss.  :so++sss+   +sn- .oso- /ss+/+ss/ -ss+sss++ss+/+o-    -sr:/ss-  +ss`sss  ooo+osss-  sCs  :ss+` oss. ossooosss+ `oso//osso/
  *  -ssssssssssss.`--.`                  `.----------------.     sso /ss. os+ /ss.  `.----sss`  +sn+/ss+` :Dr+-.-+ss.-sss-```sss/-.`     -sn:`oso .ss: sss  `.---/ss+  sss:+ss:   oss. oss:```sss`:ss:  .ss+
  * .ssssssssssss+ ..                        `.--------------.    sso `os+-ss. /ss.  /sso++sss`  +siooss:  +sso+++ooo`-ss+    ./+osso:    -sa: -ss-+so  sss `+ss++oss+  s6s+sss.   oss. oss.   sss``oss++oso.
  * :+ossssssssss: `                           `------------..`   sso  -ssos/  /ss. .sss.`.sss-` +sn:`+ss/`-sso-.`..- -ss+   `.```:sso    -sb:  +soss.  sss /ss+``:sso.`sBs`-sss-  oss. oss.   sss``oso:::.`
  *   `-+ssssssss.                               .--------`       ss+   +sso`  /ss.  +3999++sss: /sg- `/ss+.-+sssooo+ .ss+   .osoosso-    -sy:  `sss/   oso .ossoo+osso.s9s  .+ss/ oss` +ss.   oss`.sssoooo+:`
  *    `+sssssss.                              ` .------`        ```   ````   ```   `...` ... ```     ````  `....`   ```    `....``      ```   ```    ```  `...` `..` ```    ``` ```  ```    ``` +ss---:/sso
  *     -sssssss:                              .. `----.                                                                                                                                       `sss:-.-:ss+
  *      `:ossssso                              .-. .----                                                                                                                                        ./+oooo++-`
  *    `..``-+ssss:                            `---` .----`         `.-::::-` .//-                                                                                                                  ````
  * `..-----.`.:+ss:                          `----- `------..`   `:osssoooo/ /ss:
  * `----------.`.-/:`                       .------` .------.   `+ss+-`````. /ss:``..`    ``...`    ``` `...`    ``..````    `...`
  *  `------------....`                    `.-------. `-----.    /sso         /ss/ossso/  /osssso+.  +o+/ossso- `/oooooooo/ -+ooooo+`
  *   `--.....---------...```       ```` `.---------. `...-.     oss/         /sso-.-sss- :----+ss+  oss+-.:s1s :ss:``:ss/.:ss/..-sso
  *            `.------------------..```.--------.`       `      +ss+         /ss:   +ss- -+o++osso  oss.  `s9s -ss+--/ss: ssso+++sss
  *              `.--------------.```.----------`                .sss/.`   `` /ss:   +ss-:ss+..:sso  oss.   s8s `+ssooo/-  oss/-.....
  *               `---------..````.------------.                  .ossso+++o+ /ss:   +ss--sso//+sss+-oss.   s4s -sso/:::-` .oss+///+:
  *               .----..``````......-----------                    .://+//:` .::.   .::` .://:.-//:`-::`   ::: :ss+++ooss: `-:////-`
  *               .`````....`        ``--------.`                                                              `sso````.sso
  *                  ``..-.            `-...``                                                                  /ossoooss+.
  *                                                                                                             `..--..`
  *
  *
  *  +++         .+++:    /++++++++/:.     .:/+++++/: .+++/`     .+++/  ++++.      ++++.     `-/++++++/:
  *  oooo         .ooo:    +ooo:--:+ooo/   :ooo/:::/+/  -ooo+`   .ooo+`  ooooo:     .o-o`   `/ooo+//://+:
  *  oooo         .ooo:    +ooo`    :ooo-  oooo`     `   .ooo+` .ooo+`   oooooo/`   .o-o`  .oooo-`
  *  oooo         .ooo:    +ooo`    -ooo-  -ooo+:.`       .ooo+.ooo/`    ooo:/oo+.  .o-o`  +ooo.
  *  oooo         .ooo:    +ooo.`..:ooo+`   `:+oooo+:`     `+ooooo/      ooo: :ooo- .o-o`  oooo
  *  oooo         .ooo:    +ooooooooo+:`       `-:oooo-     `+ooo/       ooo/  .+oo/.o-o`  +ooo.
  *  oooo         .ooo:    +ooo-...``             `oooo      /ooo.       ooo/   `/oo-o-o`  .oooo-
  *  oooo::::::.  .ooo:    +ooo`           :o//:::+ooo:      /ooo.       ooo/     .o-o-o`   ./oooo/:::/+/
  *  +ooooooooo:  .ooo:    /ooo`           -/++ooo+/:.       :ooo.       ooo:      `.o.+      `-/+oooo+/-
  *
  *  An open-source mouth operated sip and puff joystick that enables people with limited hand function to emulate a mouse on their computer and/or smartphone.
*/

/* 
 * Copyright (c) Neil Squire Society <info@makersmakingchange.com>
 *
 * Permission is hereby granted, free of charge, to any person obtaining a copy
 * of this software and associated documentation files (the "Software"), to deal
 * in the Software without restriction, including without limitation the rights
 * to use, copy, modify, merge, publish, distribute, sublicense, and/or sell
 * copies of the Software, and to permit persons to whom the Software is
 * furnished to do so, subject to the following conditions:
 *
 * The above copyright notice and this permission notice shall be included in
 * all copies or substantial portions of the Software.
 *
 * THE SOFTWARE IS PROVIDED "AS IS", WITHOUT WARRANTY OF ANY KIND, EXPRESS OR
 * IMPLIED, INCLUDING BUT NOT LIMITED TO THE WARRANTIES OF MERCHANTABILITY,
 * FITNESS FOR A PARTICULAR PURPOSE AND NONINFRINGEMENT. IN NO EVENT SHALL THE
 * AUTHORS OR COPYRIGHT HOLDERS BE LIABLE FOR ANY CLAIM, DAMAGES OR OTHER
 * LIABILITY, WHETHER IN AN ACTION OF CONTRACT, TORT OR OTHERWISE, ARISING FROM,
 * OUT OF OR IN CONNECTION WITH THE SOFTWARE OR THE USE OR OTHER DEALINGS IN
 * THE SOFTWARE.
 */

//TITLE: LipSync_Gaming_Firmware
//AUTHOR: MakersMakingChange
//VERSION: 3.0 (27 Jun 2022)
//Copyright Neil Squire Society 2016-2022.

#include <EEPROM.h>
#include "Joystick.h"

//***OUTPUT ACTIONS***// - DO NOT CHANGE
// These are the different actions the LipSync can perform based on different sip and puff inputs.
#define OUTPUT_NOTHING              (int)0             // No action
#define OUTPUT_BUTTON_ONE           (int)1             // Press and release button one or button X1(Left USB)/View(Right USB) in XAC
#define OUTPUT_BUTTON_TWO           (int)2             // Press and release button two or button X2(Left USB)/Menu(Right USB) in XAC
#define OUTPUT_BUTTON_THREE         (int)3             // Press and release button three or button LS(Left USB)/RS(Right USB) in XAC
#define OUTPUT_BUTTON_FOUR          (int)4             // Press and release button four or button LB(Left USB)/RB(Right USB) in XAC
#define OUTPUT_BUTTON_FIVE          (int)5             // Press and release button five or button A(Left USB)/X(Right USB) in XAC
#define OUTPUT_BUTTON_SIX           (int)6             // Press and release button six button B(Left USB)/Y(Right USB) in XAC
#define OUTPUT_JOYSTICK_HOME_RESET  (int)7             // Initiates the Joystick home reset routine to reset center position. 
#define OUTPUT_JOYSTICK_CALIBRATION (int)8             // Initiates the Joystick calibration to calibrate joystick range and reset center position.

//***OUTPUT MAPPING***// - CUSTOMIZABLE
//These values can be changed to remap different output actions to different input actions
#define ACTION_SHORT_PUFF   OUTPUT_BUTTON_ONE          // Default: Press and release button one or button X1(Left USB)/View(Right USB) in XAC
#define ACTION_SHORT_SIP    OUTPUT_BUTTON_TWO          // Default: Press and release button two or button X2(Left USB)/Menu(Right USB) in XAC  
#define ACTION_LONG_PUFF    OUTPUT_BUTTON_FIVE         // Default: Press and release button five or button A(Left USB)/X(Right USB) in XAC
#define ACTION_LONG_SIP     OUTPUT_BUTTON_SIX          // Default: Press and release button six or button B(Left USB)/Y(Right USB) in XAC
#define ACTION_VLONG_PUFF   OUTPUT_JOYSTICK_HOME_RESET // Default: Initiates the Joystick home reset routine to reset center position. 
#define ACTION_VLONG_SIP    OUTPUT_NOTHING             // Default: No action

//***CUSTOMIZABLE VARIABLES***//
#define ROTATION_ANGLE 0                          // CCW Rotation angle between Screen "up" to LipSync "up" {0,90,180,270} [degrees]

#define PUFF_PRESSURE_THRESHOLD_DEFAULT (byte)10  // Pressure sip and puff threshold [percentage]
#define SIP_PRESSURE_THRESHOLD_DEFAULT  (byte)10  // Pressure sip and puff threshold [percentage]
#define PUFF_COUNT_THRESHOLD_MED 150              // Threshold between short and medium puff input [cycle counts]
#define PUFF_COUNT_THRESHOLD_LONG 750             // Threshold between medium and long puff [cycle counts]
#define SIP_COUNT_THRESHOLD_MED 150               // Threshold between short and medium puff input [cycle counts]
#define SIP_COUNT_THRESHOLD_LONG 750              // Threshold between medium and long puff in [cycle counts]

#define SENSITIVITY_COUNTER (byte)5 			        // Default sensitivity level
#define JOYSTICK_DELAY 5                          // Current joystick delay [ms]
#define DEBUG_MODE_DELAY (int)150                 // The delay used in debug mode between each reading [ms]
#define SERIAL_DELAY (byte)5                      // The delay after a serial write [ms]
#define EEPROM_WRITE_DELAY (byte)10               // The delay after an EEPROM write [ms]
#define PRESSURE_HANDLER_DELAY (byte)5            // The delay added between pressure read cycles [ms] 
#define JOYSTICK_BUTTON_DELAY 150                 // The delay after a joystick button press before release
#define BUTTON_LONG_PRESS_TIME 2000               // The time required to press a button to change button mode
#define BUTTON_DIGITAL_MODE 1                     // The digital button mode
#define BUTTON_ANALOG_MODE 2                      // The analog button mode

//*** DRIFT REDUCTIONS ***// CHANGE WITH CAUTION
#define JOYSTICK_DEADBAND 30                      // Joystick deadband {ADC steps]
#define CHANGE_DEFAULT_TOLERANCE 3                // The tolerance in changes between current reading and previous reading [ADC steps]

//***DON'T CHANGE THESE CONSTANTS***//
#define LIPSYNC_MODEL (byte)2                     // LipSync Gaming
#define LIPSYNC_VERSION (byte)30                  // LipSync Version
#define SIP_PRESSURE_THRESHOLD_MIN (byte)10       // Minimum Pressure sip and puff threshold [percentage]
#define SIP_PRESSURE_THRESHOLD_MAX (byte)50       // Maximum Pressure sip and puff threshold [percentage]
#define PUFF_PRESSURE_THRESHOLD_MIN (byte)10      // Minimum Pressure sip and puff threshold [percentage]
#define PUFF_PRESSURE_THRESHOLD_MAX (byte)50      // Maximum Pressure sip and puff threshold [percentage]
#define INPUT_ACTION_COUNT 6                      // Number of available sip and puff input types  
#define JOYSTICK_LIFT_THRESOLD 400                // Opposite FSR value nearing liftoff during purposeful movement [ADC steps]
#define JOYSTICK_MAX_DEADZONE 250                 // Joystick maximum allowed deadzone {ADC steps]
#define BUTTON_MODE BUTTON_DIGITAL_MODE           // Set button mode ( 1 = Digital button mode , 2 = Analog button mode )
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

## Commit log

2019-09-17 Updated GameStik project to LipSync Gaming
    [LipSync_Button.STL, LipSync_Front_Housing.STL, LipSync_Gaming_BOM.csv, LipSync_Gaming_BOM.xlsx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]
2019-09-20 Added the updated LipSync Manual, LipSync Gaming User Guide, LipSync Gaming Startup Guide, and LipSync Gaming BOM File.
    [LipSync_Gaming_BOM.csv, LipSync_Gaming_BOM.xlsx]
2019-10-01 Updated to V2.3
    - The shell is slightly longer and the rear portion is slightly wider to accommodate a greater range of USB cables. The cut-out near the mounting hole is also larger and longer to prevent the threade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
    - A recess has been added to the bottom to provide a less conspicuous location to apply any labelling.
    - The rear portion of the shell is larger and has greater surface area which should help mitigate any bed adhesion issues.
    - The cylindrical portions that house the springs have been lengthened and a catch was added that should retain the springs once they are pressed in. These changes should help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
    [LipSync_Button.STL]
2019-10-01 Added PCB files Version 2.71 with updated MMC Logo.
    [LipSync_Interface_Board.brd, LipSync_Interface_Board.sch]
2019-10-01 Updated PCB version number in readme file.
2020-04-15 Added PCB board gerber files.
    [LipSync_Interface_Board.brd, LipSync_Interface_Board.sch, LipSync_Joystick_Board.brd, LipSync_Joystick_Board.sch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]
2020-04-15 Updated readme file
    Added the links to PCB board gerber files.
2020-05-08 Added the PCB Fabrication Manual
2022-06-09 Updated documentation
    [LipSync_Gaming_BOM.csv, LipSync_Gaming_BOM.xlsx, LipSync_Rear_Housing.stl]
2022-06-09 Added back STL files
    [LipSync_Button.stl, LipSync_Front_Housing.STL, LipSync_Joystick_Base.STL, LipSync_Joystick_Front.STL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]
2022-06-28 Updated Documents
    [LipSync_Gaming_BOM.csv, LipSync_Gaming_BOM.xlsx]
2022-07-18 Updated rear housing STL file
2022-07-18 Resolved merge conflict
    [LipSync_Rear_Housing.STL]

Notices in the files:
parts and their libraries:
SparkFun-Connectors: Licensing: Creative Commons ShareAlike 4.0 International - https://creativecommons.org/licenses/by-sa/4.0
